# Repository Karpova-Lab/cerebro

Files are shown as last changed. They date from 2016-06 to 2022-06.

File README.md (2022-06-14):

# Cerebro Wireless Optogenetics System v2

Detailed documentation at [https://karpova-lab.github.io/cerebro/](https://karpova-lab.github.io/cerebro/)

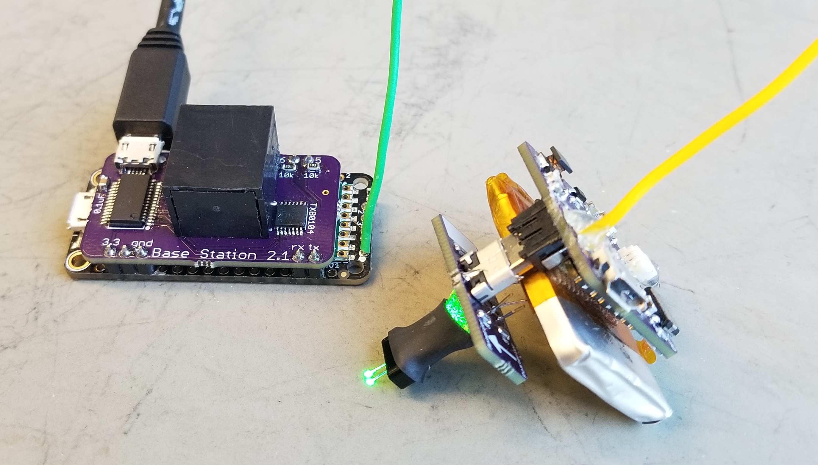
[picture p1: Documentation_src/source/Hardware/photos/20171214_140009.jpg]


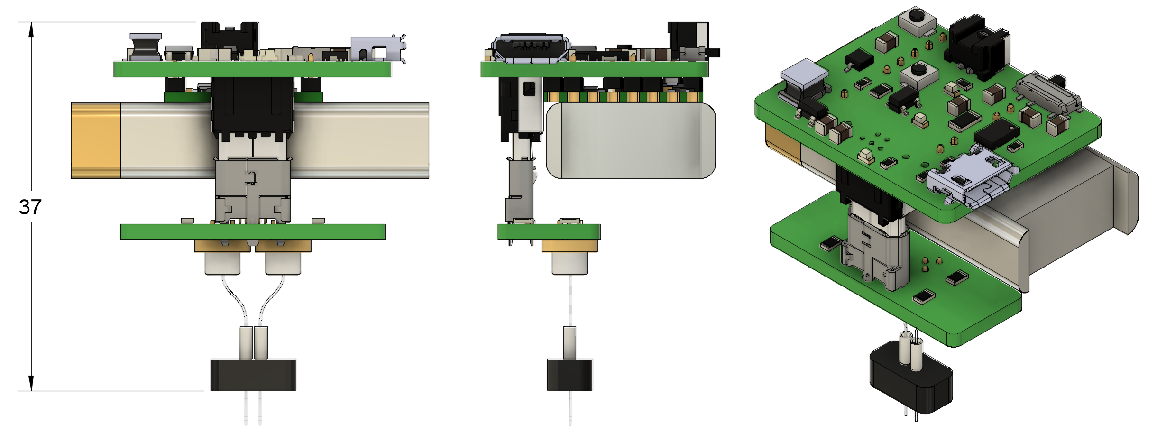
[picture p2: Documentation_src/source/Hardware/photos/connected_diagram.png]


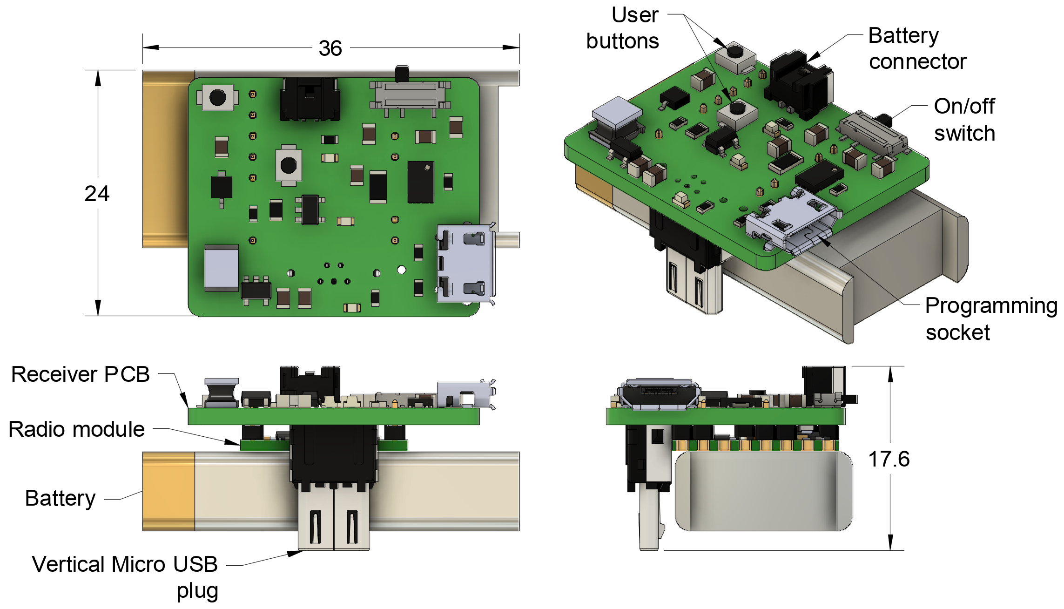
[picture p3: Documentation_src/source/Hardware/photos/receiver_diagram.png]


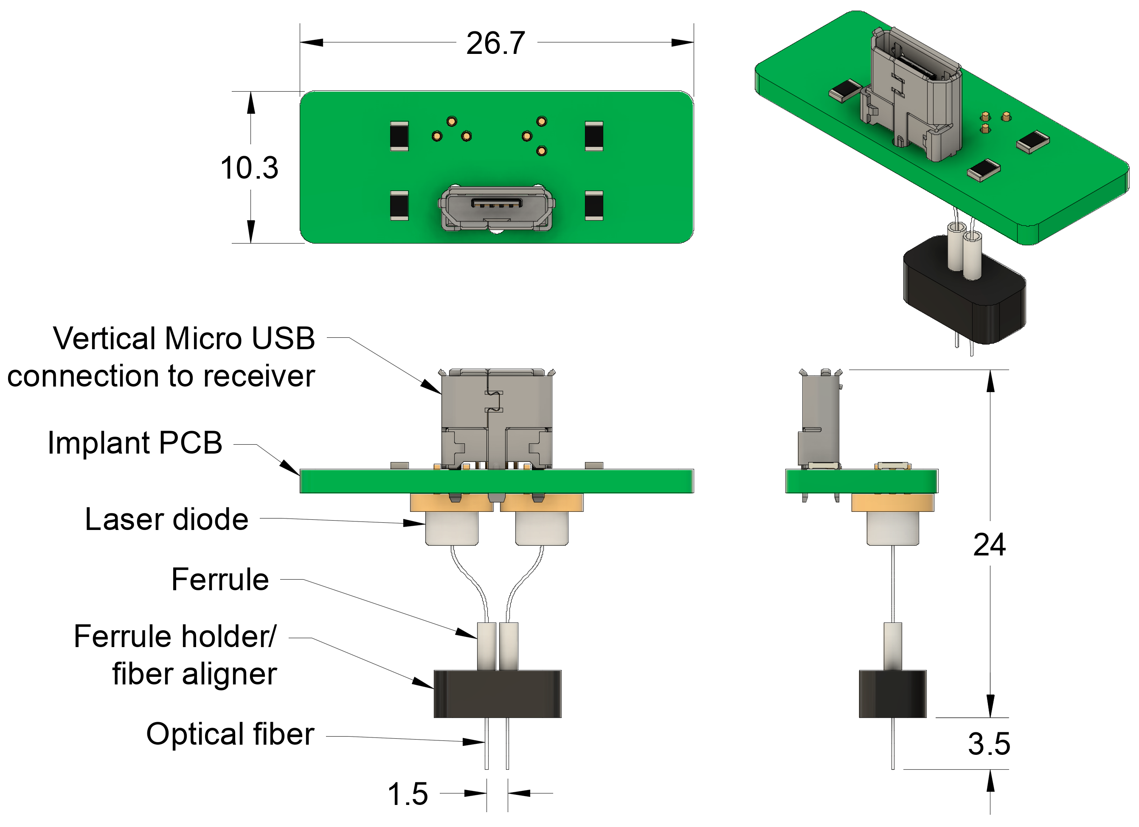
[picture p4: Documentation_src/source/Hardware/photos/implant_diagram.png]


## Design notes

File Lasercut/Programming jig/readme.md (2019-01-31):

# Bill of Materials
- [Spear head pogo pins](https://www.adafruit.com/product/394)
- [Toggle clamp](https://www.adafruit.com/product/2457)
- M6 x 20mm Pan head screws
- M6 nuts
- 1/8" Acrylic

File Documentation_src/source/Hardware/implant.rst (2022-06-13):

:github_url: https://github.com/Karpova-Lab/cerebro

============
Head Implant
============
.. include:: Characters/isogrk1.txt
.. include:: Characters/mmlalias.txt
.. include:: Characters/isopub.txt

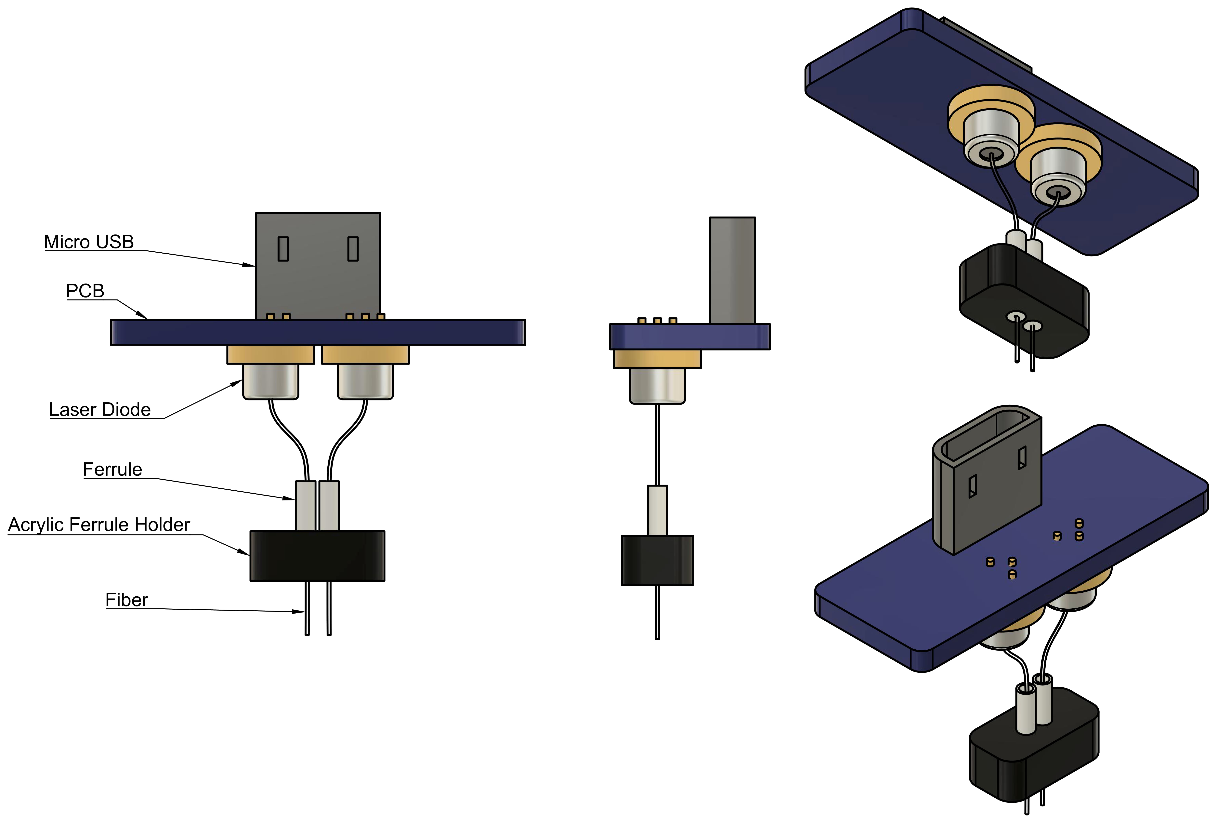
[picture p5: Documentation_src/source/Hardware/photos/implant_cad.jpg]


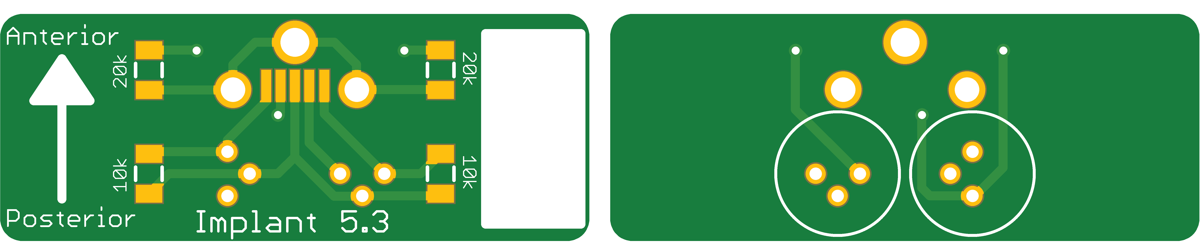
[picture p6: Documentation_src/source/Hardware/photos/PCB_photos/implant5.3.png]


  `Click Here for Design Files <https://github.com/Karpova-Lab/cerebro/tree/master/PCB%20Files/Implant%205.3>`_ 

.. _implantTools:

Required Tools
==============
  * Ruler
  * Soldering iron
  * Tweezers   
  * `Fiber gripper <https://www.thorlabschina.cn/thorproduct.cfm?partnumber=BFG1>`_ 
  * `Fiber stripper <https://www.thorlabs.com/thorProduct.cfm?partNumber=T12S21>`_
  * `Fiber cleaver <http://www.fiberinstrumentsales.com/fis-lynx-precision-cleaver-with-fiber-basket.html>`_
  * `3-axis fiber launch system <http://www.thorlabs.com/thorproduct.cfm?partnumber=MBT612D/M>`_
  * `Power meter <https://www.thorlabs.com/thorproduct.cfm?partnumber=PM121D>`_ and `photodiode sensor <https://www.thorlabs.com/thorproduct.cfm?partnumber=S121C>`_
  * `Adjustable DC Power Supply <https://www.amazon.com/KORAD-KD3005D-Precision-Adjustable-Regulated/dp/B00FPU6G4E/ref=sr_1_2?s=hi&ie=UTF8&qid=1521832325&sr=1-2&keywords=korad+power+supply&dpID=41CeDR0WTPL&preST=_SY300_QL70_&dpSrc=srch>`_ 
  * `Ultraviolet light <https://www.amazon.com/TaoTronics-TT-FL001-Flashlight-Blacklight-Ultraviolet/dp/B00RV8PREI/ref=sr_1_1?ie=UTF8&qid=1484071557&sr=8-1&keywords=B00RV8PREI>`_

Bill of Materials
=================
+-----+-----------------------------+----------------------------------------------------------------+-------------------------------------------------------------------------------------------------------------------------+
| Qty | Description                 | Datasheet                                                      | Order Link                                                                                                              | 
+=====+=============================+================================================================+=========================================================================================================================+
| 1   | Implant PCB                 |  :download:`Implant 5.3<Datasheets/implant_5.3.pdf>`           | `OSH Park <https://oshpark.com/shared_projects/k8Ikpli6>`__                                                             | 
+-----+-----------------------------+----------------------------------------------------------------+-------------------------------------------------------------------------------------------------------------------------+
| 1   | Laser Diode                 |  :download:`PLT5 520_B1_2_3<Datasheets/green_laser_diode.pdf>` | `World Star Tech <http://www.worldstartech.com/products/laser-diodes/green-laser-diode-osram/>`__                       | 
+-----+-----------------------------+----------------------------------------------------------------+-------------------------------------------------------------------------------------------------------------------------+
| 1   | Fiber                       | F-MBB                                                          | `Newport <https://www.newport.com/p/F-MBB>`__                                                                           | 
+-----+-----------------------------+----------------------------------------------------------------+-------------------------------------------------------------------------------------------------------------------------+
| 1   | UV curing adhesive          |  :download:`NOA 68<Datasheets/uv_adhesive.pdf>`                | `Norland Products <https://www.norlandproducts2.com/adhesives/adproductsdetail_header_removed.asp?Prdid=68>`__          | 
+-----+-----------------------------+----------------------------------------------------------------+-------------------------------------------------------------------------------------------------------------------------+
| 1   | Ferrule                     |  :download:`MM-FER2007C<Datasheets/ferrule.pdf>`               | `Precision Fiber Products <https://precisionfiberproducts.com/pfp-lc-1-25mm-od-multimode-ceramic-zirconia-ferrules/>`__ | 
+-----+-----------------------------+----------------------------------------------------------------+-------------------------------------------------------------------------------------------------------------------------+
| 1   | Epoxy                       |  :download:`T120023C<Datasheets/epoxy.pdf>`                    | `Fiber Instrument Sales <http://www.fiberinstrumentsales.com/fis-room-cure-epoxy-2-grams.html>`__                       | 
+-----+-----------------------------+----------------------------------------------------------------+-------------------------------------------------------------------------------------------------------------------------+
| 2   | Micro USB vertical socket   |  :download:`1051330011<Datasheets/usb_socket_vertical.pdf>`    | `Digi-Key <https://www.digikey.com/products/en?keywords=WM10134CT-ND>`__                                                | 
+-----+-----------------------------+----------------------------------------------------------------+-------------------------------------------------------------------------------------------------------------------------+
| 2   | Heat shrink tubing          |  :download:`HSTTV12-Y<Datasheets/heatshrink.pdf>`              | `Digi-Key <https://www.digikey.com/products/en?x=0&y=0&lang=en&site=us&keywords=298-11559-ND>`__                        | 
+-----+-----------------------------+----------------------------------------------------------------+-------------------------------------------------------------------------------------------------------------------------+
| 2   | 0603 10 k\ |OHgr| Resistor  |                                                                |                                                                                                                         | 
+-----+-----------------------------+----------------------------------------------------------------+-------------------------------------------------------------------------------------------------------------------------+
| 1   | 0603 20 k\ |OHgr| Resistor  |                                                                |                                                                                                                         | 
+-----+-----------------------------+----------------------------------------------------------------+-------------------------------------------------------------------------------------------------------------------------+

Assembly Instructions
=====================
Prepare Fiber
-------------
#. Tape down the fiber
#. Use a fiber stripper to remove the outer blue jacket from the fiber

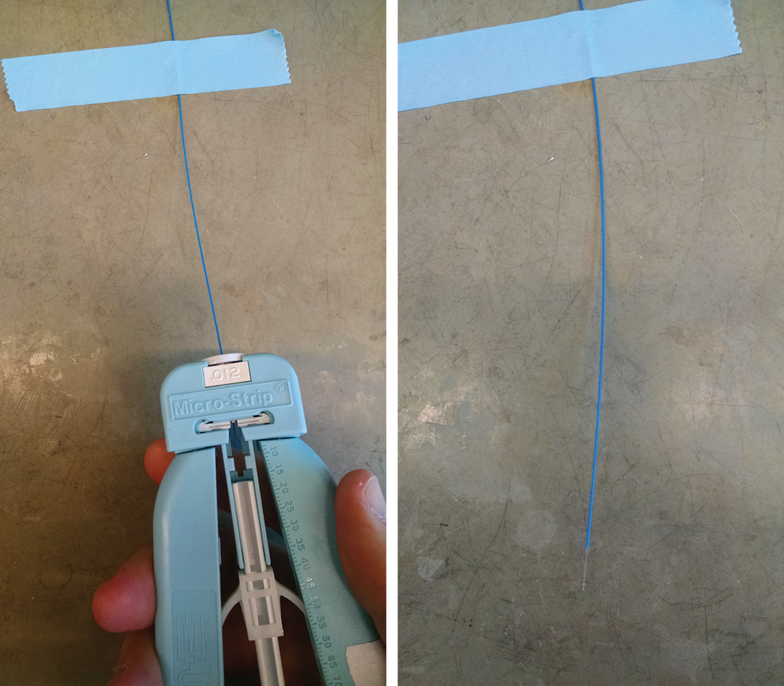
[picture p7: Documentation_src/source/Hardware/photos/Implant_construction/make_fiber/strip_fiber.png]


3. Using a fiber cleaver, cut off the end of fiber to make a clean tip
#. Continue cutting the fiber into ~16mm pieces

Align Fiber
-----------
#. Insert laser diode into connector
#. Place connector in alignment jig
#. Place fiber in alignment jig
#. Turn on the power meter and connect to computer over usb
#. Open up the `Thorlabs' Power Meter Software <https://www.thorlabs.com/software_pages/ViewSoftwarePage.cfm?Code=PM100x>`_ 
#. Establish the USB connection with Power meter by selecting the device and clicking "OK"

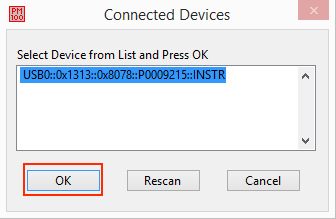
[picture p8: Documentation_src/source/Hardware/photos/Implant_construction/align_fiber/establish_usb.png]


7. Adjust the following settings:

  - Range: 12mW
  - Wave: 520nm
  - Log Configuration

    - No of Samples: 20,000
    - Interval Time: 0.1

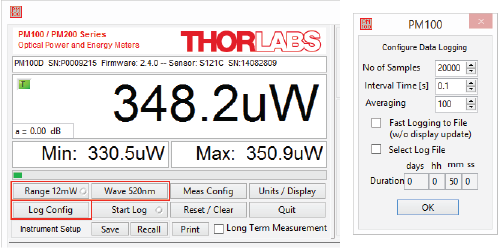
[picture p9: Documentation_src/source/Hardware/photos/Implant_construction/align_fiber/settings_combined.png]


8. Click ``Start Log``



9. Set the power supply to 8.0 volts with a current limit of 300 mA
#. Provide power to the laser diode by pressing the "on/off" button
#. While watching the power graph update, use the `3-axis fiber launch system <http://www.thorlabs.com/thorproduct.cfm?partnumber=MBT612D/M>`_ to adjust the x, y, and z alignment of the fiber with respect to the laser diode.
#. When you are happy with the alignment, apply UV curing adhesive to the fiber/laserdiode junction.
#. Cure the adhesive using UV light

Fiber Guide Construction
------------------------
A fiber guide is needed to ensure that the fibers are at a precise distance apart, and are parallel. The distance will depend on what area of the brain is being targeted. Below are files for 1.5 mm and 2.74 mm gap between fibers.

- :download:`Fiber guide_1,5mm gap.dxf<../../../Lasercut/Fiber guide/Fiber guide_1,5mm gap.dxf>` 
- :download:`Fiber guide_1,5mm gap.ai<../../../Lasercut/Fiber guide/Fiber guide_1,5mm gap.ai>` 
- :download:`Fiber guide_2,74mm gap.ai<../../../Lasercut/Fiber guide/Fiber guide_2,74mm gap.ai>` 

The laser cutter speed and power settings may need to be tweaked to get a good fit for the the ceramic ferrules.

#. Insert the ceramic ferrules into the acrylic fiber guide. The flat side of the ferrules should be flush with the face of the acrylic.

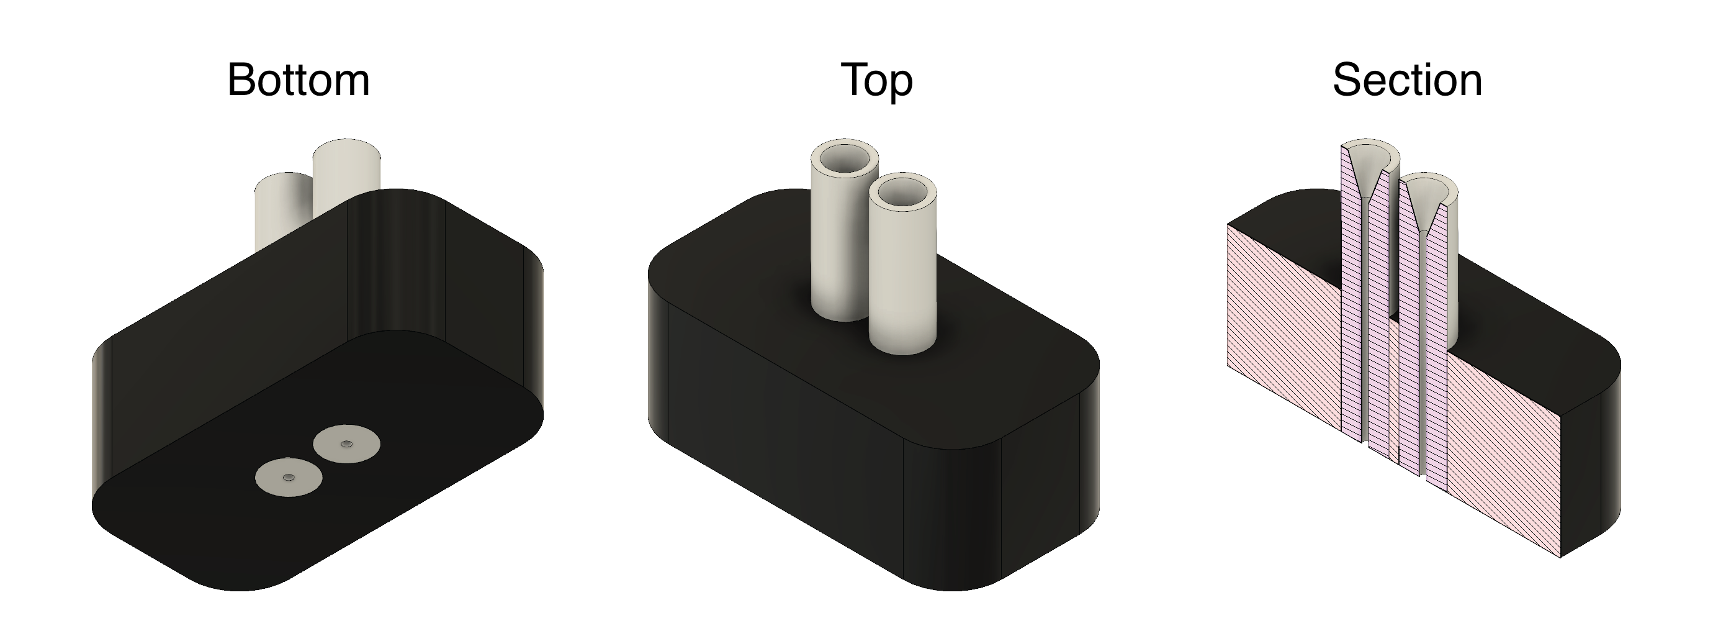
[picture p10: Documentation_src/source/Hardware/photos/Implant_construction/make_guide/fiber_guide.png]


Combine PCB, Laser Diodes, and Fiber Guide
------------------------------------------
#. Solder the vertical microusb connector onto the PCB
#. Solder 1 leg of each laser diode onto the PCB
#. Bend the laser diodes toward eachother so the tips of the fiber slightly intersect near their tips
#. Solder the remaining legs of the laser diodes
#. Cut ~10mm of heat shrink tubing and slide it onto one of the laser diodes
#. Apply heat to the heat shrink tubing

.. Warning::
   Heat can weaken the UV glue that is used to attach the fiber. Be careful not to apply too much heat for too long as you may risk weakening the glue, causing the fiber to move out of alignment or detach completely.

7. Slide the fiber guide onto the two fibers. Adjust the 
#. Surround the fibers and laser diodes with epoxy
#. Place heatshrink tubing around the clear epoxy section of the implant
#. Place and solder the remaining resistors onto the PCB

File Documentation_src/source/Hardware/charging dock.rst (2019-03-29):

:github_url: https://github.com/Karpova-Lab/cerebro

=============
Charging Dock 
=============

.. include:: Characters/isogrk1.txt
.. include:: Characters/mmlalias.txt

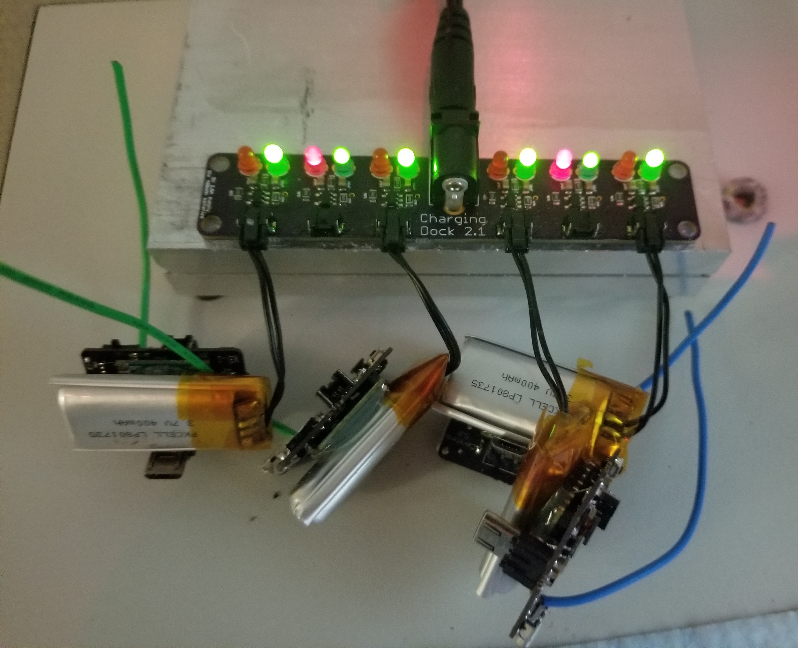
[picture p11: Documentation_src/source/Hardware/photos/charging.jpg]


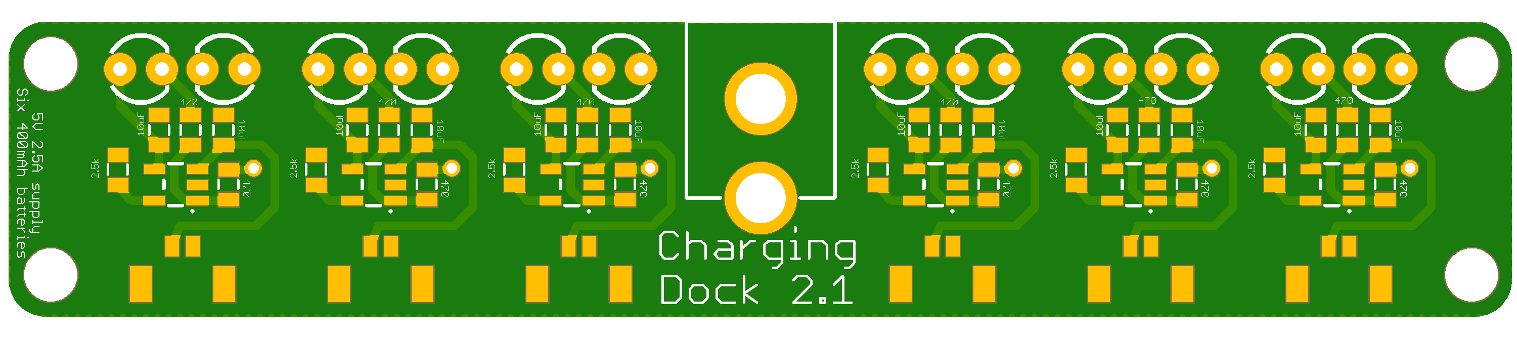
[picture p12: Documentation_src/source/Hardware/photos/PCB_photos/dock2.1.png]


  `Click Here for Design Files <https://github.com/Karpova-Lab/cerebro/tree/master/PCB%20Files/Charging%20Dock%202.1>`_ 

Bill of Materials
=================

+-----+------------------------------+------------------------------------------------------------------+----------------------------------------------------------------------------------------------------+
| Qty | Description                  | Datasheet                                                        | Order Link                                                                                         | 
+=====+==============================+==================================================================+====================================================================================================+
| 1   | Charging Dock PCB            |  :download:`Charging Dock 2.0<Datasheets/charging_dock_2.0.pdf>` | `OSH Park <https://oshpark.com/shared_projects/hz6upCEq>`__                                        | 
+-----+------------------------------+------------------------------------------------------------------+----------------------------------------------------------------------------------------------------+
| 1   | Molex Micro-Lock socket      |  :download:`5055670271<Datasheets/microlock_socket.pdf>`         | `Digi-Key <https://www.digikey.com/products/en?keywords=WM17038CT-ND>`__                           | 
+-----+------------------------------+------------------------------------------------------------------+----------------------------------------------------------------------------------------------------+
| 6   | Lipoly Charging IC           |  :download:`MCP73831T-2ACI/OT<Datasheets/lipo_charger.pdf>`      | `Digi-Key <https://www.digikey.com/products/en?keywords=%09MCP73831T-2ACI%2FOTCT-ND>`__            | 
+-----+------------------------------+------------------------------------------------------------------+----------------------------------------------------------------------------------------------------+
| 1   | DC Barrel Power Jack         |  :download:`PJ-037A<Datasheets/power_jack.pdf>`                  | `Digi-Key <https://www.digikey.com/products/en?keywords=cp-037a-nd>`__                             | 
+-----+------------------------------+------------------------------------------------------------------+----------------------------------------------------------------------------------------------------+
| 1   | 5V 2.5A Power Supply         |  :download:`SWI12-5-N-P5R<Datasheets/power_supply.pdf>`          | `Digi-Key <https://www.digikey.com/product-detail/en/cui-inc/SWI12-5-N-P5R/102-3425-ND/5287234>`__ | 
+-----+------------------------------+------------------------------------------------------------------+----------------------------------------------------------------------------------------------------+
| 6   | Green LED                    |  :download:`151031VS06000<Datasheets/led_3mm_green.pdf>`         | `Digi-Key <https://www.digikey.com/products/en?keywords=732-5008-ND>`__                            | 
+-----+------------------------------+------------------------------------------------------------------+----------------------------------------------------------------------------------------------------+
| 6   | Red LED                      |  :download:`151031SS06000<Datasheets/led_3mm_red.pdf>`           | `Digi-Key <https://www.digikey.com/products/en?keywords=732-5006-ND>`__                            | 
+-----+------------------------------+------------------------------------------------------------------+----------------------------------------------------------------------------------------------------+
| 12  | 0805 470 \ |OHgr| Resistor   |                                                                  |                                                                                                    | 
+-----+------------------------------+------------------------------------------------------------------+----------------------------------------------------------------------------------------------------+
| 6   | 0805 2.5 K\ |OHgr| Resistor  |                                                                  |                                                                                                    | 
+-----+------------------------------+------------------------------------------------------------------+----------------------------------------------------------------------------------------------------+
| 12  | 0805 10 |mgr|\F Capacitor    |                                                                  |                                                                                                    | 
+-----+------------------------------+------------------------------------------------------------------+----------------------------------------------------------------------------------------------------+

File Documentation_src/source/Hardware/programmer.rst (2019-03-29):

:github_url: https://github.com/Karpova-Lab/cerebro

==============
Pogo Connector
==============

.. include:: Characters/isogrk1.txt
.. include:: Characters/mmlalias.txt

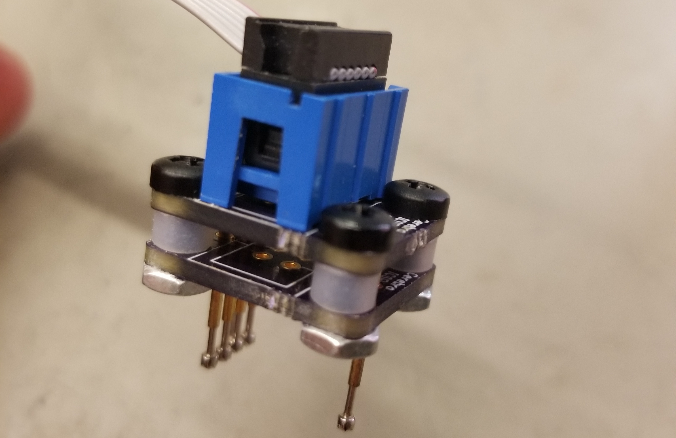
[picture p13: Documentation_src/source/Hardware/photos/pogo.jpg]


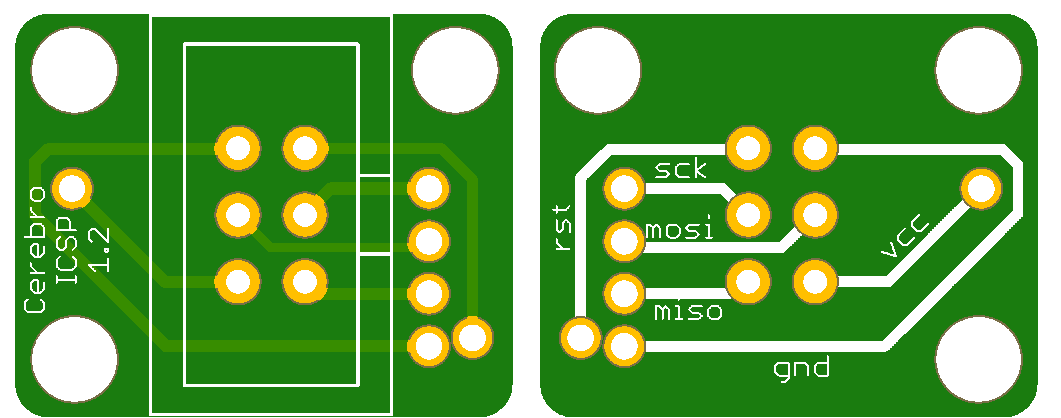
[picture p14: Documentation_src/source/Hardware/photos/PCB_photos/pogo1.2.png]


  `Click Here for Design Files <https://github.com/Karpova-Lab/cerebro/tree/master/PCB%20Files/Cerebro%20ICSP%201.2>`_ 

Bill of Materials
=================

+-----+----------------------+-------------------------------------------------------+-------------------------------------------------------------------------+
| Qty | Description          | Datasheet                                             | Order Link                                                              | 
+=====+======================+=======================================================+=========================================================================+
| 2   | Programmer PCB       | Cerebro ICSP 1.2                                      | `OSH Park <https://oshpark.com/shared_projects/PXMM4F8R>`__             | 
+-----+----------------------+-------------------------------------------------------+-------------------------------------------------------------------------+
| 1   | 6 Pin Socket         |  :download:`75869-331LF<Datasheets/ICSP_socket.pdf>`  | `Digi-Key <https://www.digikey.com/products/en?keywords=609-5122-ND>`__ | 
+-----+----------------------+-------------------------------------------------------+-------------------------------------------------------------------------+
| 5   | Spear Head Pogo Pin  | 394                                                   | `Adafruit <https://www.adafruit.com/product/394>`__                     | 
+-----+----------------------+-------------------------------------------------------+-------------------------------------------------------------------------+
| 1   | Needle Head Pogo Pin | 2430                                                  | `Adafruit <https://www.adafruit.com/product/2430>`__                    | 
+-----+----------------------+-------------------------------------------------------+-------------------------------------------------------------------------+
| 3   | M3 x 0.5 Screw       |  :download:`92492A717<Datasheets/m3_nylon_screw.pdf>` | `McMaster-Carr <https://www.mcmaster.com/#92492A717>`__                 | 
+-----+----------------------+-------------------------------------------------------+-------------------------------------------------------------------------+
| 3   | Nylon Spacer         |  :download:`93657A203<Datasheets/nylon_spacer.pdf>`   | `McMaster-Carr <https://www.mcmaster.com/#93657A203>`__                 | 
+-----+----------------------+-------------------------------------------------------+-------------------------------------------------------------------------+
| 3   | M3 Nut               |  :download:`90695A033<Datasheets/m3_nut.pdf>`         | `McMaster-Carr <https://www.mcmaster.com/#90695A033>`__                 | 
+-----+----------------------+-------------------------------------------------------+-------------------------------------------------------------------------+

Use the Pogo connector to :ref:`burn a bootloader onto Cerebro <burn boot>`

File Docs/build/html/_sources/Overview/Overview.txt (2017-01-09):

================
System Overview
================
.. include:: isogrk1.txt
.. include:: mmlalias.txt

Features
--------

Open Source = Flexible
  All code and CAD is available so you can make changes and improvements to anything you want!

Low Latency
  Less than 3ms latency between a trigger command being sent and the laser diodes being powered on.

Wirelessly Adjustable Waveforms
  Cerebro can be produce :ref:`customizable waveforms<waveform parameters>` with 1ms resolution. The waveform parameters can be adjusted wirelessly, even while the animal is behaving.

Laser Diodes
  Laser diodes are more powerful than LEDs. Instead of using a LED coupled to a large fiber, you can use a laser diode coupled to smaller fiber and get equivalent light power output but with reduced brain tissue damage.
  Bilateral implants have been capable of up to 15 mW per fiber-coupled laser diode or 450 mW/mm\ :sup:`2` (tested with two 520 nm laser diodes coupled to 200 |mgr|\m diameter fibers and powered by two 105 mAh lipo batteries).

.. Keep in mind the limiting factor of the tested implant wasn't the laser diodes, but rather the peak current supply of the batteries.

.. This means you can substitute a LED coupled to a large fiber, with a laser diode coupled to smaller (less brain damaging) fiber.
.. By coupling high power laser diodes with small fibers, one can get the same amount of light power
.. as LEDs coupled with large fibers, but instead use a high power laser diode with a small fiber. Using smaller fibers results in less brain tissue damage.
..
.. One can get equal light power by coupling high power laser diodes with small fibers, as one

Low Material Cost
  Hardware BOMs are provided, with a total estimated cost of $300. The software is free.

.. csv-table::
  :header: "Subsystem", "Material Cost ($)", "Assembly Time (hours)"
  :widths: 1,1,1

  Cerebro,30 , 1
  Head Implant (bilateral),190,4
  Base Station,5,1
  IR Remote,40,1
  Arduino + Utility Shield,30,1
  Downloader Cord,5,1
  Xavier, FREE, 0
  ,
  **Total**,**$300**,**9 hours**

Commercial Alternatives
-----------------------
Here are some commercial products that also provide wireless optogenetics:

| `Eicom Teleopto <https://eicomusa.com/teleopto/>`_
| `Kendall Research Systems <http://www.kendallresearchsys.com/>`_
| `Neurolux <http://www.neurolux.org/products/>`_
| `Triangle Biosystems <http://www.trianglebiosystems.com/s-series-systems.html>`_
|

.. .. csv-table::
..   :header: "Product", "Cost ($)", "Features"
..   :widths: 1,1,1
..
..   `Eicom Teleopto <https://eicomusa.com/teleopto/>`_ , "4,500", "Very similar to Cerebro. Uses battery and IR triggering."
..   `Kendall Research Systems <http://www.kendallresearchsys.com/>`_ , "20,000", "Uses wireless power. Includes 3-axis accelerometer"
..   `Neurolux <http://www.neurolux.org/products/>`_,
..   `Triangle Biosystems <http://www.trianglebiosystems.com/s-series-systems.html>`_,

Cerebro
-------

.. image:: cerebro.jpg
  :align: center
  :scale: 20 %

Cerebro is a rechargable wireless receiver that connects to a head implant assembly. Cerebro receives commands from a :ref:`base station` and delivers power to
the laser diodes on the head implant, resulting in light being emitted through the optical fibers into the brain. The
intensity and waveform of the emitted light can be adjusted wirelessly during an experiment (:ref:`How to change Pulse Parameters <pulse change header>`).
All commands sent to Cerebro are saved along with timestamps to onboard non-volatile memory.

:doc:`More info... <../Hardware/cerebro>`

Head Implant
------------

.. image:: implant.jpg
  :align: center
  :scale: 10 %

The head implant assembly consists of two laser diodes coupled to optical fibers. Also included is a photoresistor that is used as feedback
to maintain a constant light output.

:doc:`More info... <../Hardware/implant>`

.. _base station:

Base Station
------------
.. image:: base_station.jpg
  :align: center
  :scale: 15 %

The Base Station is responsible for emitting infrared light signals to communicate wirelessly with Cerebro (exactly like a TV remote).
It is connected by USB to a Windows computer, where commands can be sent and events can be logged using :ref:`Xavier <xavier>`.
Base Station can also be controlled directly by `TTL <https://learn.sparkfun.com/tutorials/logic-levels#ttl-logic-levels>`_ signals going into
its RJ45 connector. A high TTL signal on pin3 of the RJ45 causes a trigger signal to be emitted, and a high TTL signal on pin2 causes
a stop signal to be emitted. Events will still be logged by Xavier even when triggered by a TTL.

:doc:`More info... <../Hardware/implant>`

.. _utility shield:

Utility Shield
--------------
.. image:: utility_shield.jpg
  :align: center
  :scale: 15 %

The Utility Shield connects to an `Arduino Uno <https://www.arduino.cc/en/main/arduinoBoardUno>`_ and is used to flash programs to a variety of AVR microcontrollers.
It can flash the ATtiny84 DIP used by the IR Remote and Charging Dock, the ATtiny84 SOIC used by Cerebro, the ATtiny85 DIP used by the Base Station, and the ATmega328P
used by the IR Remote. The shield also provides a charging port for Cerebro that has a green/red charging indicator light.

:doc:`More info... <../Hardware/utility shield>`

Charging Dock
-------------
.. image:: charging_dock.jpg
  :align: center
  :scale: 20 %

The Charging Dock provides ports for charging up to 4 Cerebro receivers at one time.
An OLED display shows the voltages of the batteries being charged.
A red indicator LED is lit while Cerebro is charging, and turns off once Cerebro is fully charged.

:doc:`More info... <../Hardware/charging dock>`

IR Remote
---------

.. image:: IR_remote.jpg
  :align: center
  :scale: 20 %

The IR Remote is a handheld remote that can be used to send commands to Cerebro.
Information including battery status, current parameters, and ID number can be checked by plugging a Cerebro Receiver into the IR Remote.

:doc:`More info... <../Hardware/remote>`

.. _cord:

Downloader Cord
---------------
.. image:: downloader.jpg
  :align: center
  :scale: 15 %

The Downloader Cord is used for serial communication between a computer and Cerebro. Once connected to Cerebro's
micro usb port, it can be used for downloading log data off of Cerebro's EEPROM, or it can be used to display
messages when Cerebro is in debugging mode.

:doc:`More info... <../Hardware/downloader cord>`

.. _xavier:

Xavier
------

.. image:: xavier_demo.png
    :align: center
    :scale: 80 %

Xavier is a GUI for sending and logging Base Station commands. Since communication between Cerebro and Base Station is unidirectional, in order to truly know what occurs throughout an experiment,
every event that is received by Cerebro is also saved to an onboard log.  After an experiment is complete, Cerebro's onboard logfile can be
downloaded into Xavier. The two log files can then be saved and analyzed to confirm that everything that was sent by Base Station was in fact received and executed by Cerebro.
Xavier provides an easy interface for sending parameter changes and can also be used a debugging tool.

:doc:`More info... <../Software/Xavier>`

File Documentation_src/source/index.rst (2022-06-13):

:github_url: https://github.com/Karpova-Lab/cerebro

.. include:: isogrk1.txt
.. include:: mmlalias.txt

========================================
Cerebro Wireless Optogenetics System v2
========================================

Welcome! This is the hardware and software documentation of a system used for wireless `optogenetic <https://en.wikipedia.org/wiki/Optogenetics>`_ stimulation.
As an `open-source <http://www.oshwa.org/definition/>`_ project, this documentation is intended to provide exhaustive resources and detailed instructions to enable anyone to
study, replicate, share, improve and contribute back to the Cerebro Wireless Optogenetics System. 

This project was developed by Andy Lustig in the `Karpova Lab <https://www.janelia.org/lab/karpova-lab>`_ at HHMI's Janelia Research Campus. If you have questions or comments, you can post them on the `discussions page <https://github.com/Karpova-Lab/cerebro/discussions>`_.

.. Note::
  You are currently viewing documentation for the **radio controlled Version 2 system**. 
  To view documentation for the **infrared controlled Version 1 system**, click the button below.

  .. raw:: html

    <div style="text-align:center; margin-bottom:24px">
      <a href="https://cerebro.readthedocs.io/en/1.0/" style="
      background-color: #6ab0de;
      border: none;
      color: white;
      padding: 10px 10px;
      text-align:center;
      text-decoration: none;
      display: inline-block;
      font-size: 20px;
      font-weight: bold;
      line-height: 1.1;
      border-radius:15px">
      Version 1 (infrared) documentation</a>
    </div>

.. _overview:

Features
========

Wireless Radio
  - **Low Latency** -  Less than 1.5 ms latency between a trigger command being sent and the laser diodes being powered on.
  - **2-Way Communication** - Base Station can send messages to start, extend, or interrupt light stimulation on Cerebro. Cerebro can send acknowledgment messages that commands are received, as well as battery status updates.
  - **Good Signal Range** - At least 20m, doesn't need line of sight. (The radio module that Cerebro uses has been shown to have ranges greater than 500m with the right antennas https://lowpowerlab.com/forum/rf-range-antennas-rfm69-library/rfm69hw-range-test!/)
  - **Wirelessly Adjustable Waveforms** - Cerebro can produce :ref:`customizable waveforms<waveform parameters>` with 1ms resolution. The waveform parameters can be adjusted wirelessly, even while the animal is behaving.

Laser Diodes
  - **High Power** - Laser diodes are more powerful than LEDs. Instead of using an LED coupled to a large fiber, you can use a laser diode coupled to smaller fiber and get equivalent light power output but with reduced brain tissue damage.
  - **Independent Bilateral Control of Intensity** -  Each laser diode has its own control circuitry, enabling you to turn on either diode at different times and/or different intensities. Intensity ramp-downs can be used to prevent post illumination rebounds in neural activity (https://www.cell.com/neuron/pdf/S0896-6273(17)30602-5.pdf).

Open Source
  * **Flexible** - All code and CAD is available so you can make changes and improvements to anything you want!
  * **Low Cost** - Hardware BOMs are provided, with a total estimated material cost of ~$200 (~$40 per Cerebro, ~$120 per bilateral head implant, ~$40 per Base Station). The software is free.
..    .. csv-table::
..      :header: "Subsystem", "Material Cost ($)", "Assembly Time (hours)"
..      :widths: 1,1,1
..    
..      Cerebro,40 , 2
..      Head Implant (bilateral),120,4
..      Base Station,40,.5
..      Xavier, FREE, 0
..      **Total**,**$145**,**6.5 hours**
  
.. **Technical Specifications**
.. 
.. .. csv-table::
..   :header: "Parameter", "Test Condition", "Value", "Unit"
..   :widths: 3,3,3,3
.. 
..   Weight,,13.2, g
..   Dimensions, Receiver, 0.68 x 0.74 x 0.062 , in
..             , Implant, 1.05 x 0.40 x 0.75, in
..   :download:`Battery Life <photos/battery new.html>`, "520nm, 8mW 3s pulse, 6 pulses/min ", 4.25 (1700), "hours (pulses)"
..   Recharge time, ,1 ,hour
..   Light Wavelength, ":download:`PLT5 520<Datasheets/PL520_B1.pdf>` (Green)", "520","nm"
..   :download:`Trigger Latency <photos/Signal_Breakdown.png>`, , 3.5 |pm|\  0.1, ms
..   Rise Time, , 10 , ms
..   Fiber Diameter, , 200,|mgr|\m
..   Light Output (per fiber) ,520 nm diode coupled to 200 |mgr|\m fiber, 0 to 15 |pm|\  0.5, mW
..   Input Voltage, , 3.5 to 4.2, V
..   Idle Current, ,"28","mA"

Block Diagram
=============

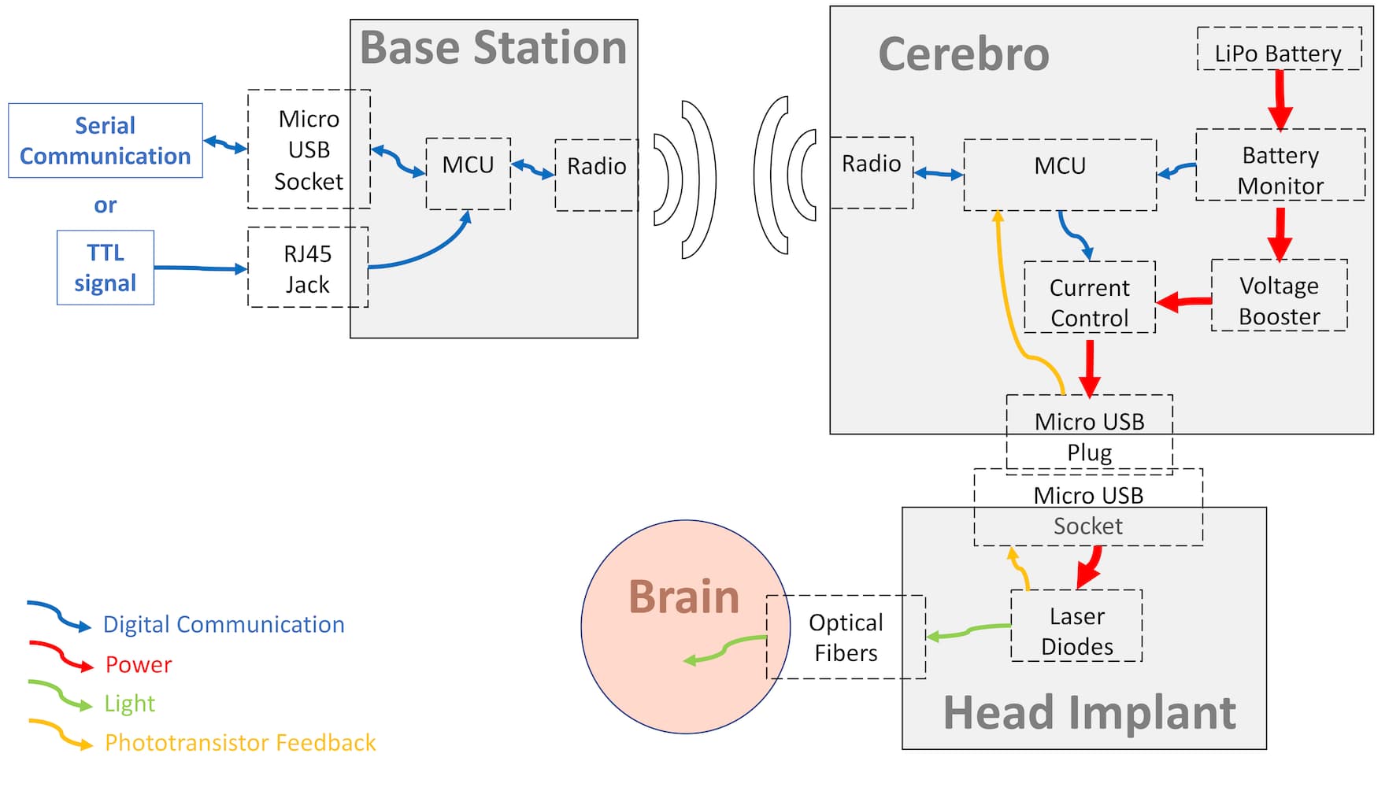
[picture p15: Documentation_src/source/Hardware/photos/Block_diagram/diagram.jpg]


System Components
=================
Cerebro
-------
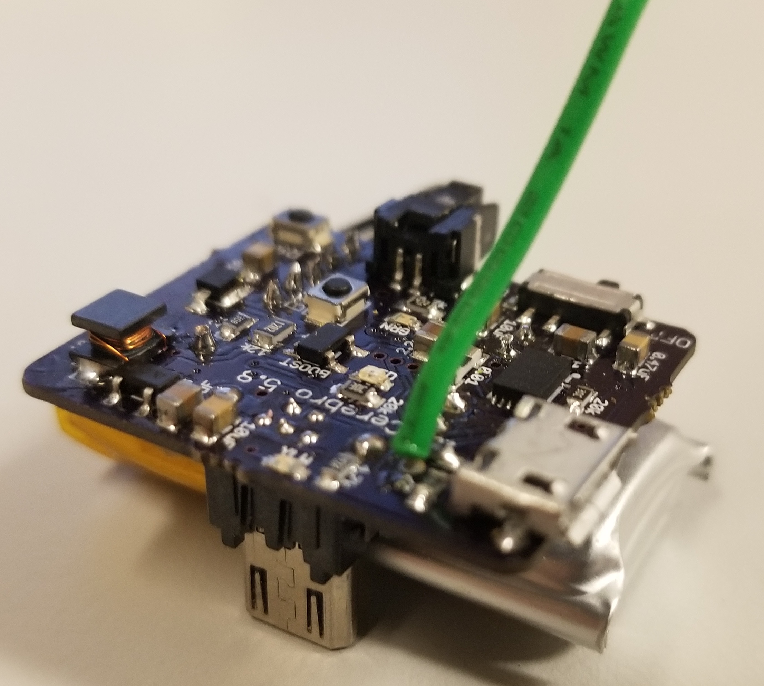
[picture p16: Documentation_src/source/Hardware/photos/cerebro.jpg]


Cerebro is a rechargable battery powered wireless receiver that connects to a head implant assembly. Cerebro receives commands from a :ref:`base station` and delivers power to
the laser diodes on the head implant, resulting in light being emitted through the optical fibers into the brain. The
intensity and waveform of the emitted light can be adjusted wirelessly during an experiment (:ref:`Edit Waveform Parameters <waveform parameters>`).

:doc:`More info... <Hardware/cerebro>`

Head Implant
------------


The head implant assembly consists of two laser diodes coupled to optical fibers. Both laser diodes include an integrated phototranistor that is used as feedback
to maintain a constant light output. The laser diodes can be independently controlled and can output arbitrary waveforms with millisecond resolution.

:doc:`More info... <Hardware/implant>`

.. _base station:

Base Station
------------
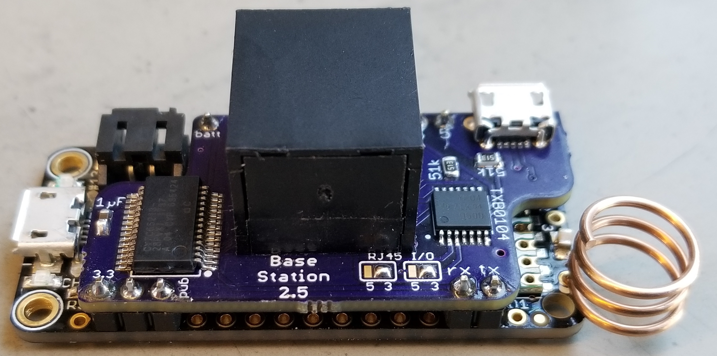
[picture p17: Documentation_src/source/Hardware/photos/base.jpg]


The Base Station is responsible for communicating wirelessly with Cerebro via radio.
It is connected by USB to a Windows computer, where commands can be sent and events can be logged using serial communication with Xavier.
Base Station can also be controlled directly by `TTL <https://learn.sparkfun.com/tutorials/logic-levels#ttl-logic-levels>`_ signals going into
its RJ45 connector. A high TTL signal on pin3 of the RJ45 causes a trigger command to be sent, and a high TTL signal on pin2 causes
a stop command to be sent.

:doc:`More info... <Hardware/base station>`

Charging Dock
-------------


The Charging Dock has the same battery connectors as Cerebro and can charge up to 6 Cerebro lipo batteries at once. 

:doc:`More info... <Hardware/charging dock>`

Xavier Software
---------------
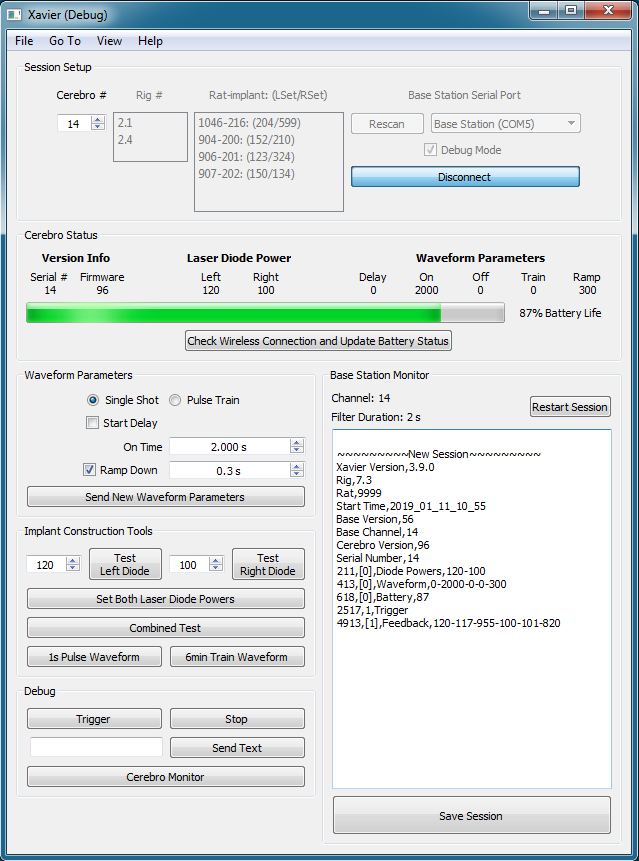
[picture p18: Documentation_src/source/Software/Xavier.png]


Xavier is a GUI for sending and logging Base Station commands. 
Xavier provides an easy interface for sending parameter changes and can also be used as a debugging tool.

:doc:`More info... <../Software/Xavier>`

Alternative Commerical Systems
==============================

Here are some commercial products that also provide wireless optogenetics:

- `Doric OSE System <https://neuro.doriclenses.com/collections/wireless-recording>`_ 
- `Eicom Teleopto <https://eicomusa.com/teleopto/>`_
- `Neurolux <http://www.neurolux.org/>`_
- `Multichannel Systems <https://www.multichannelsystems.com/products/wireless-systems>`_

Documentation Outline
=====================
.. toctree::
  :caption: Hardware

  Hardware/cerebro.rst
  Hardware/implant.rst
  Hardware/base station.rst
  Hardware/charging dock.rst
  Hardware/programmer.rst

.. toctree::
  :caption: Software

  Software/Xavier.rst

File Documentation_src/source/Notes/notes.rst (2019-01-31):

:github_url: https://github.com/Karpova-Lab/cerebro

====================
Additional Resources
====================

Soldering Tips
==============

Through Hole Soldering
----------------------

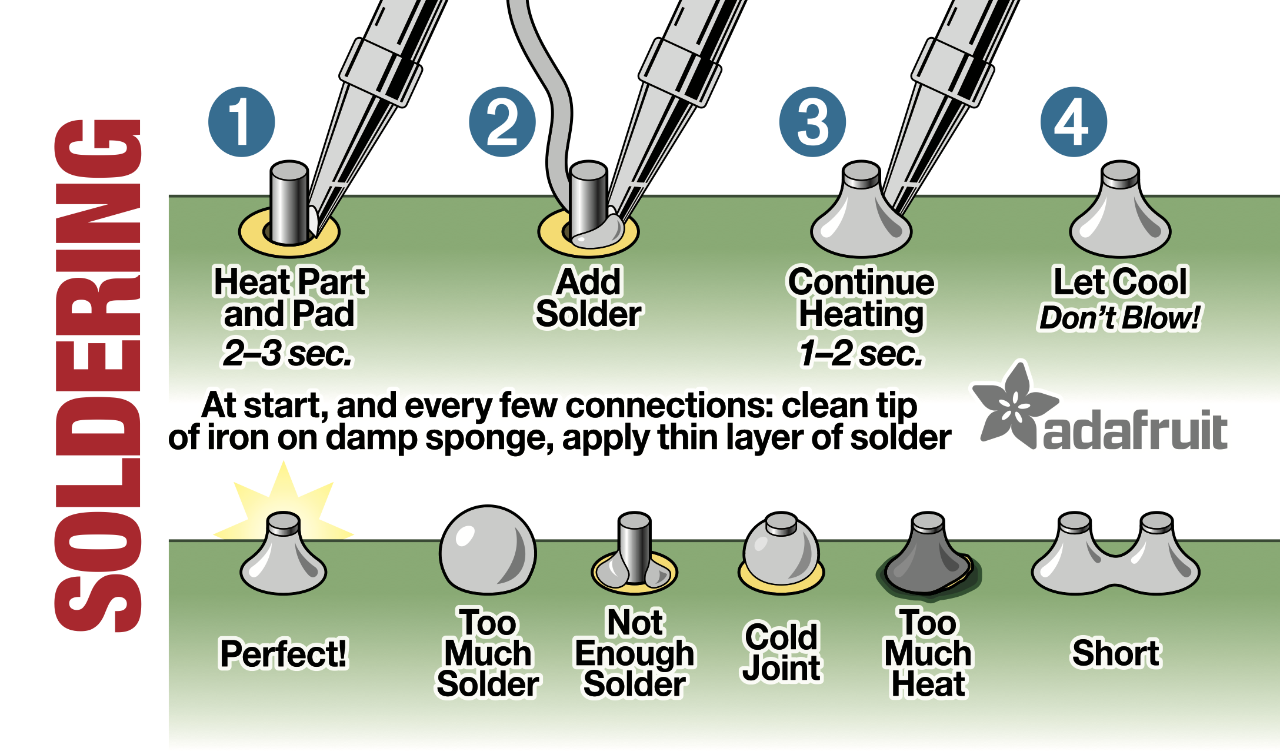
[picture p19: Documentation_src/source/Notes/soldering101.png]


Surface Mount Soldering
-----------------------

.. raw:: html

  <div style="text-align:center;margin-bottom:24px">
    <iframe width="560" height="315" src="https://www.youtube.com/embed/b9FC9fAlfQE?rel=0" frameborder="0" allowfullscreen></iframe>
  </div>

Git
===

Using Git
---------

Here is an nice introduction to what Git is: `Tutorial by Atlassian <https://www.atlassian.com/git/tutorials/what-is-version-control>`_

If you don't want to use the command line for running Git commands, I recommend downloading `SourceTree <https://www.sourcetreeapp.com/>`_ to use as a GUI.

Cloning the Cerebro repository from Github
------------------------------------------

From the Command Line
`````````````````````

Create a new folder into which you want to clone the repository

.. code::

   mkdir mylocalrepo

Navigate into the folder you just created and then clone the contents of the Cerebro repository from Github

.. code::

   cd mylocalrepo/
   git clone https://github.com/alustig3/Cerebro.git .

From a Mac terminal it will look like this:

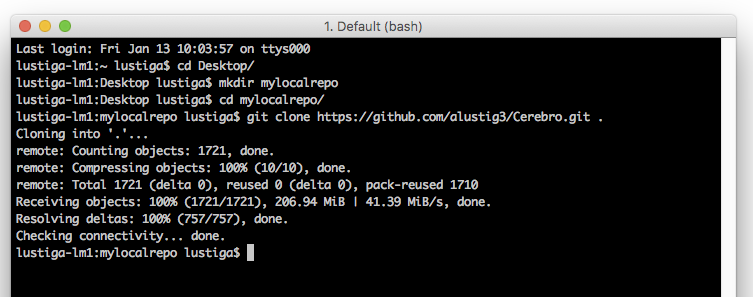
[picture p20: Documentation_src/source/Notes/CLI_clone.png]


Using SourceTree
````````````````
1. Navigate to File -> New/Clone
2. Paste ``https://github.com/alustig3/Cerebro.git`` as the source/URL
3. The files now exist locally on your computer

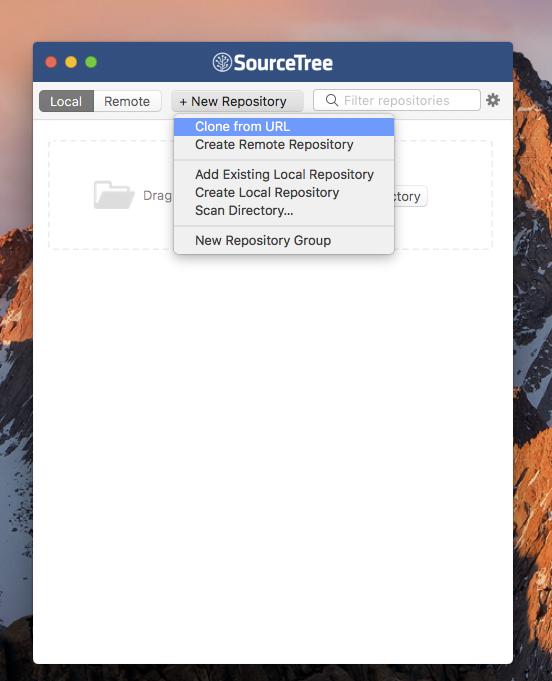
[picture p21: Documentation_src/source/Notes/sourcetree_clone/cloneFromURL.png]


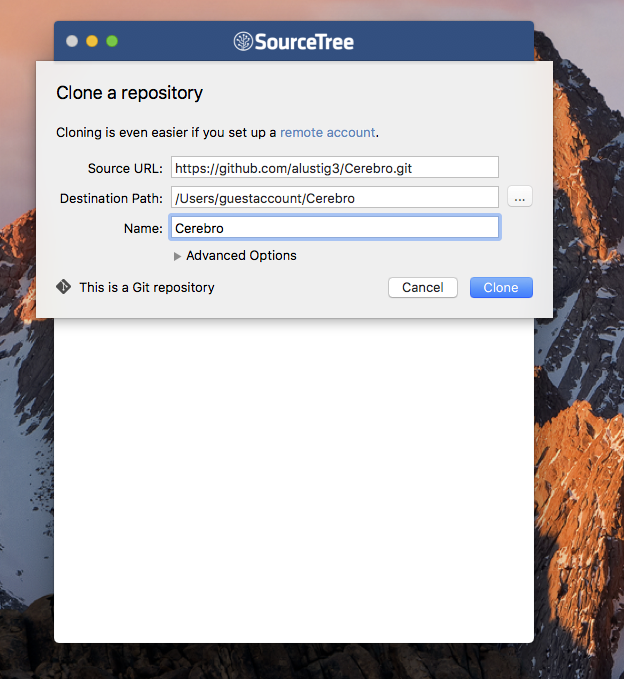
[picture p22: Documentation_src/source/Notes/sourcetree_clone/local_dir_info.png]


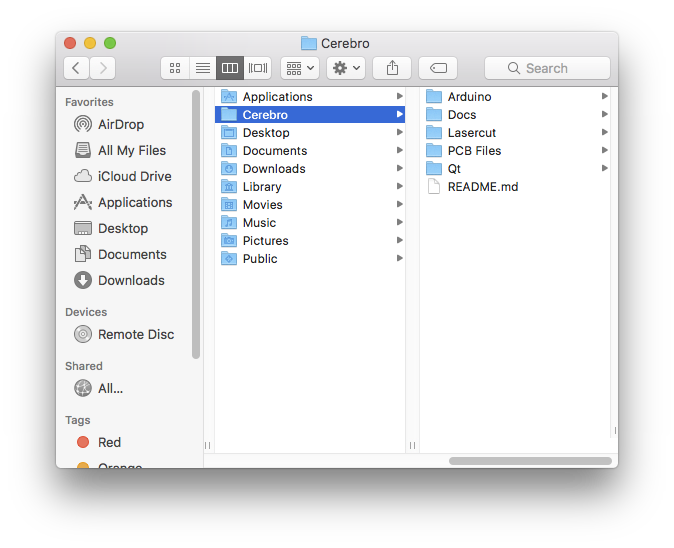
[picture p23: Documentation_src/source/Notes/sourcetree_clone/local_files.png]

  
Circuit Board Design
====================

EAGLE CAD design software is used for all of the circuit boards in the Cerebro Wireless Optogenetics System. To get started with editing PCB files, check out the following tutorials:

- `Jeremy Blum's EAGLE Tutorials <http://www.jeremyblum.com/category/eagle-tutorials/>`_
- `Sparkfun's Using EAGLE Series <https://learn.sparkfun.com/tutorials/using-eagle-schematic>`_

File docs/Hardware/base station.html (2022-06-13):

- Docs »
- Base Station
- Cerebro on GitHub (https://github.com/Karpova-Lab/cerebro)

Next Previous

# Base Station¶



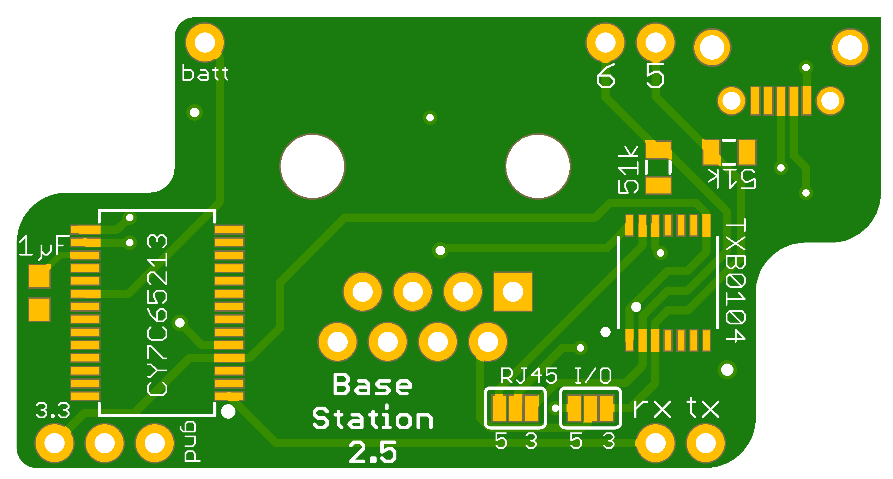
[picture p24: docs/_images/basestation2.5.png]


Click Here for Design Files (https://github.com/Karpova-Lab/cerebro/tree/master/PCB%20Files/Base%20Station%202.5)¶

## Bill of Materials¶

Qty | Description | Datasheet | Order Link
1 | Base Station PCB | Base Station 2.5 | OSH Park (https://oshpark.com/shared_projects/qpPpopqr)
1 | Feather 32u4 RFM69HCW | 3076 | Digi-Key (https://www.digikey.com/products/en?keywords=1528-1663-ND)
1 | USB to Serial Converter | CY7C65213-28PVXI | Digi-Key (https://www.digikey.com/products/en?keywords=%09CY7C65213-28PVXI-ND)
1 | Voltage Level Translator | TXB0104PWR | Digi-Key (https://www.digikey.com/products/en?keywords=296-21929-1-nd)
1 | Micro USB horizontal socket | 10118194-0001LF | Digi-Key (https://www.digikey.com/products/en?keywords=609-4618-1-ND)
1 | Antenna | HA.31.A | Digi-Key (https://www.digikey.com/products/en?keywords=931-1452)
2 | 0805 51 kΩ Resistor

## Downloads¶

- Cypress USB Driver (http://www.cypress.com/documentation/software-and-drivers/usb-serial-software-development-kit)
- Adafruit Feather Driver (https://learn.adafruit.com/adafruit-feather-32u4-basic-proto/using-with-arduino-ide)

Next Previous

© Copyright 2015-2022, Andy Lustig Last updated on Jun 13, 2022.

Built with Sphinx (http://sphinx-doc.org/) using a theme (https://github.com/rtfd/sphinx_rtd_theme) provided by Read the Docs (https://readthedocs.org).

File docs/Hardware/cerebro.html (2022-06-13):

- Docs »
- Cerebro
- Cerebro on GitHub (https://github.com/Karpova-Lab/cerebro)

Next Previous

# Cerebro¶

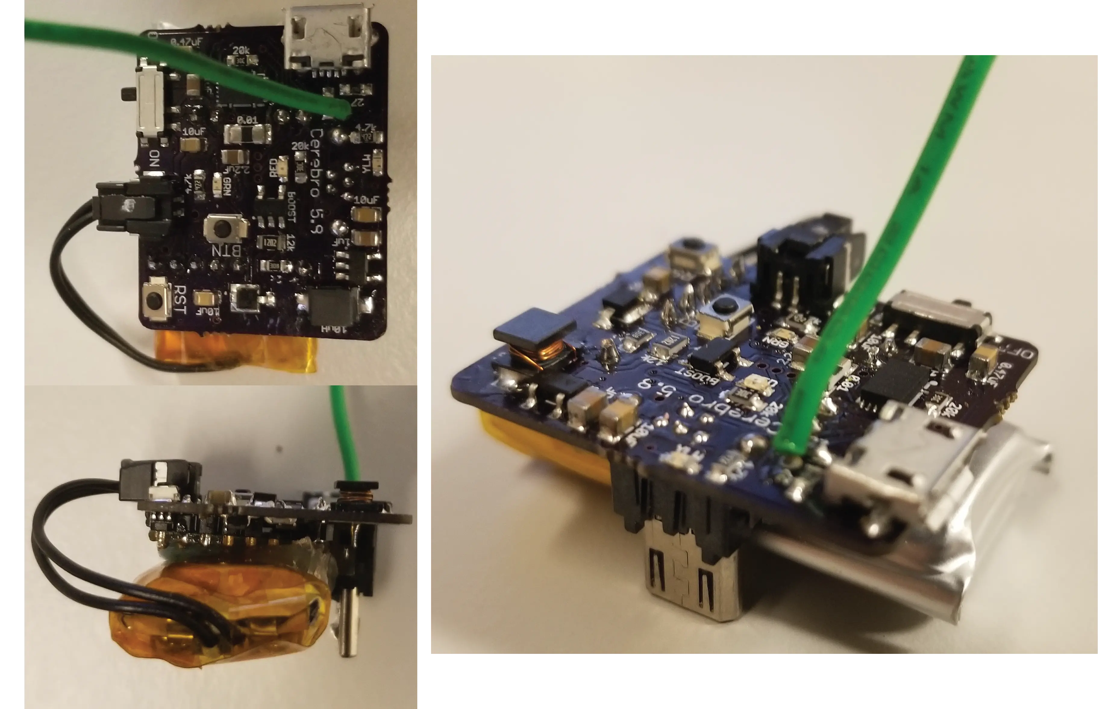
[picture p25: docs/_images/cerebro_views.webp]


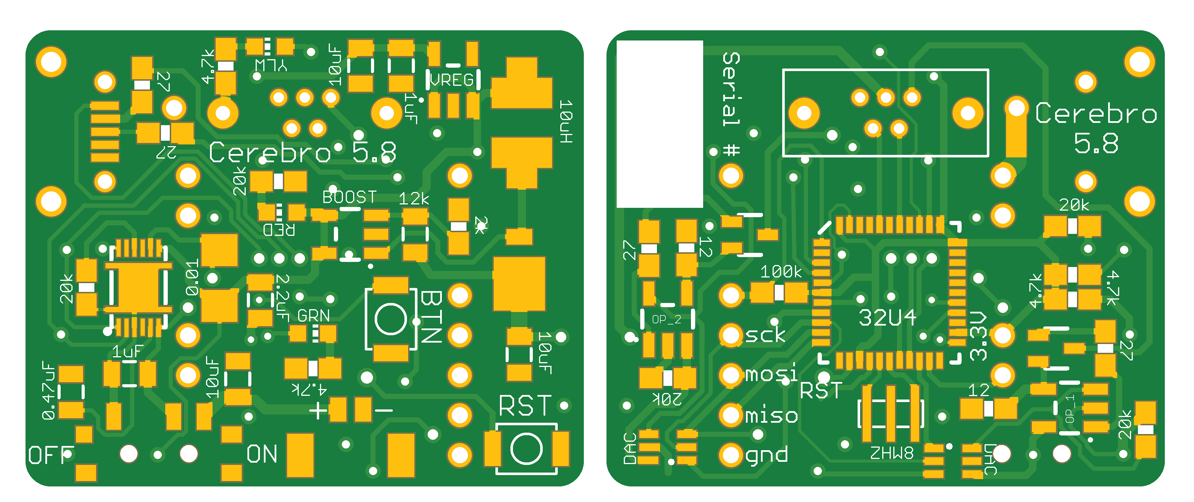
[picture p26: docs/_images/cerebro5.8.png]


Click Here for Design Files (https://github.com/Karpova-Lab/cerebro/tree/master/PCB%20Files/Cerebro%205.8)¶

## Bill of Materials¶

Qty | Description | Part # / Datasheet | Order Link
1 | Cerebro PCB | Cerebro 5.8 | OSH Park (https://oshpark.com/shared_projects/ASxhDBJv)
1 | 550 mAh Battery | 602835 | Amazon (https://www.amazon.com/s?k=B09DPNX4KP)
1 | 915 MHz Radio | RFM69HCW | LowPowerLab (https://lowpowerlab.com/shop/product/158)
1 | Microcontroller | ATMEGA32U4-MUR | Digi-Key (https://www.digikey.com/products/en?keywords=ATMEGA32U4-MURCT-ND)
1 | 8 MHz Resonator | CSTCE8M00G55-R0 | Digi-Key (https://www.digikey.com/products/en?keywords=490-1195-1-ND)
1 | 3.3V Linear Regulator | AP2112K-3.3TRG1 | Digi-Key (https://www.digikey.com/products/en?keywords=%09AP2112K-3.3TRG1DICT-ND)
1 | Fuel Gauge | BQ27441DRZR-G1B | Digi-Key (https://www.digikey.com/product-detail/en/texas-instruments/BQ27441DRZR-G1B/296-39942-1-ND/5177819)
2 | DAC (12-Bit) | LTC2630ACSC6-LZ12#TRMPBF | Digi-Key (https://www.digikey.com/product-detail/en/linear-technology/LTC2630ACSC6-LZ12-TRMPBF/LTC2630ACSC6-LZ12-TRMPBFCT-ND/1643783)
2 | Op Amp | OPA237NA/3K | Digi-Key (https://www.digikey.com/products/en?keywords=296-26265-1-ND)
2 | NPN Transistor | FJX3904TF | Digi-Key (https://www.digikey.com/products/en?keywords=FJX3904TFCT-ND)
1 | Boost Converter | MIC2288YD5-TR | Digi-Key (https://www.digikey.com/products/en?keywords=576-1729-1-ND)
1 | Schottky Diode | MBRM140T3G | Digi-Key (https://www.digikey.com/products/en?keywords=MBRM140T3GOSCT-ND)
1 | 10uH Inductor | LQH43CN100K03L | Digi-Key (https://www.digikey.com/products/en?keywords=490-2519-1-ND)
2 | 2mm Pitch Male Header | M22-2510805 | Digi-Key (https://www.digikey.com/products/en?keywords=952-1992-nd)
1 | Slide Switch | PCM12SMTR | Digi-Key (https://www.digikey.com/products/en?keywords=401-2016-1-nd)
2 | Momentary Button | B3U-1000P | Digi-Key (https://www.digikey.com/products/en?keywords=sw1020ct)
1 | Micro USB vertical plug | ZX20-B-5S-UNIT(30) | Digi-Key (https://www.digikey.com/products/en?keywords=H125237-ND)
1 | Micro USB shielding | ZX20-B-SLDC | Digi-Key (https://www.digikey.com/products/en?keywords=H11496CT-ND)
1 | Micro USB horizontal socket | 10118194-0001LF | Digi-Key (https://www.digikey.com/products/en?keywords=609-4618-1-ND)
1 | Molex Micro-Lock socket | 5055670271 | Digi-Key (https://www.digikey.com/products/en?keywords=WM17038CT-ND)
1 | Molex Micro-Lock plug with wire | 0151360206 | Digi-Key (https://www.digikey.com/products/en?keywords=WM17161-ND)
1 | Red LED (0603) | LTST-C191KRKT | Digi-Key (https://www.digikey.com/products/en?keywords=160-1447-1-ND)
1 | Amber LED (0603) | LNJ437W84RA | Digi-Key (https://www.digikey.com/products/en?keywords=%09LNJ437W84RACT-ND)
1 | Green LED (0603) | SML-D12M8WT86 | Digi-Key (https://www.digikey.com/products/en?keywords=511-1578-1-ND)
1 | 470 nF Capacitor (0805) | | Digi-Key (https://www.digikey.com/product-detail/en/avx-corporation/08055C474KAT2A/478-5033-1-ND/1888244)
2 | 1 μF Capacitor (0805) | | Digi-Key (https://www.digikey.com/products/en?keywords=1276-1066-1-nd)
1 | 2.2 μF Capacitor (0805) | | Digi-Key (https://www.digikey.com/products/en?keywords=587-1286-1)
3 | 10 μF Capacitor (0805) | | Digi-Key (https://www.digikey.com/product-detail/en/murata-electronics-north-america/GRM21BR61E106KA73L/490-5523-1-ND/2334919)
1 | 0.01 Ω Resistor (1206) | | Digi-Key (https://www.digikey.com/products/en?keywords=P0.01BVCT-ND)
2 | 12 Ω Resistor (0603) | | Digi-Key (https://www.digikey.com/products/en?keywords=P12.00BYCT-ND)
4 | 27 Ω Resistor (0603) | | Digi-Key (https://www.digikey.com/products/en?keywords=541-27.0SCT-ND)
1 | 2 kΩ Resistor (0603) | | Digi-Key (https://www.digikey.com/products/en?keywords=RNCP0603FTD2K00CT-ND)
3 | 4.7 kΩ Resistor (0603) | | Digi-Key (https://www.digikey.com/products/en?keywords=311-4.70KHRCT-ND)
2 | 12 kΩ Resistor (0805) | | Digi-Key (https://www.digikey.com/products/en?keywords=311-12.0KCRCT-ND)
5 | 20 kΩ Resistor (0603) | | Digi-Key (https://www.digikey.com/products/en?keywords=RNCP0603FTD20K0CT-ND)
2 | 100 kΩ Resistor (0603) | | Digi-Key (https://www.digikey.com/products/en?keywords=%09311-100KHRCT-ND)

## Programming Instructions¶

### Setup Arduino IDE¶

Follow these instructions : https://learn.adafruit.com/adafruit-feather-32u4-basic-proto/arduino-ide-setup

### Burning a Bootloader¶

Cerebro is designed to be easily reprogrammed through the onboard micro USB. However when builing a Cerebro from scratch, you must first burn a bootloader (https://www.arduino.cc/en/Tutorial/ArduinoISP) onto the microcontroller in order to later upload programs through USB.

To burn a bootloader you need an external programmer that will talk to the microntroller through the In-Circuit Serial Programmer (ISP). You can use an Arduino as your external ISP and temporarily solder wires to the Cerebro PCB. I recommmend using a USB microISP (https://www.tindie.com/products/nsayer/usb-uisp/) along with a Pogo Connector.

1. The programmer needs to connect to the ISP thru-holes (MOSI, MISO, SCK, RST, GND and 3V) on the Cerebro PCB.



2. In the Arduino IDE, select Tools->Board->”Adafruit Feather 32u4”
3. Select Tools->Programmer->”USBtinyISP” or Tools->Programmer->”ArduinoISP” if using an Arduino as the programmer
4. Select Tools->Burn Bootloader

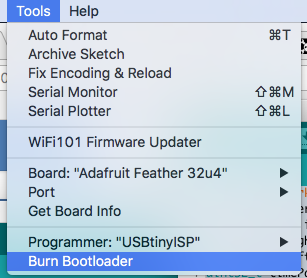
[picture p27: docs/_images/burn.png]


### Uploading Test Program¶

To test that the components on the PCB are soldered correctly and that all of the required connections are being made, we upload a test program.

1. Open testBoard.ino in the Arduino IDE.
2. Select Tools->Board->”Adafruit Feather 32u4”.
3. Under the Tools->Port menu look to see what Serial Ports are available.
4. Connect a battery to Cerebro.
5. Connect Cerebro to your computer with a usb cord and switch on Cerebro. A red LED should be lit, indicating that Cerebro is on.
6. There should now be a new serial port under the Tools->Port menu that wasn’t there in step 2. This is the Cerebro serial port, select it. If there a new serial port didn’t appear in the menu, make sure Cerebro is turned on and connected via USB. If it still doesn’t appear in the menu, the bootloader may have not been burned correctly, so try burning the bootloader again.
7. Click the upload button to upload the the testBoard firmware.
8. Open up Serial Monitor by click the magnifying glass icon.
9. Set the Serial Monitor Baud Rate to 115200 Baud.
10. Two yellow LEDs on Cerebro should be blinking and text should be appearing in the Serial Monitor.
11. Follow the instructions on the Serial Monitor. If everything is working properly then the battery monitor should be able to provide a Battery charge %.

### Uploading Firmware¶

1. Open cerebro.ino in the Arduino IDE.
2. Select Tools->Board->”Adafruit Feather 32u4”.
3. Click the upload button to upload the the Cerebro firmware.

## Assigning a Serial Number¶

A serial number is assigned to each Cerebro. When a Base Station connects to Cerebro, it communicates on the radio channel corresponding to Cerebro’s serial number. This prevents crosstalk between Base Stations and Cerebros in the case where multiple behavior sessions are being run at the same time in the same room. Each Cerebro being used should setup a unique serial number between 1 and 255 using the process below.

1. Start an Xavier session in Debug Mode. The Base Station should be connnected, and have a green check mark.



2. Click Setup New Cerebro



3. Hold down the button labeled “BTN” on Cerebro until the nearby LED blinks twice. A green checkmark should now be next to the “Cerebro Wireless Connection”.

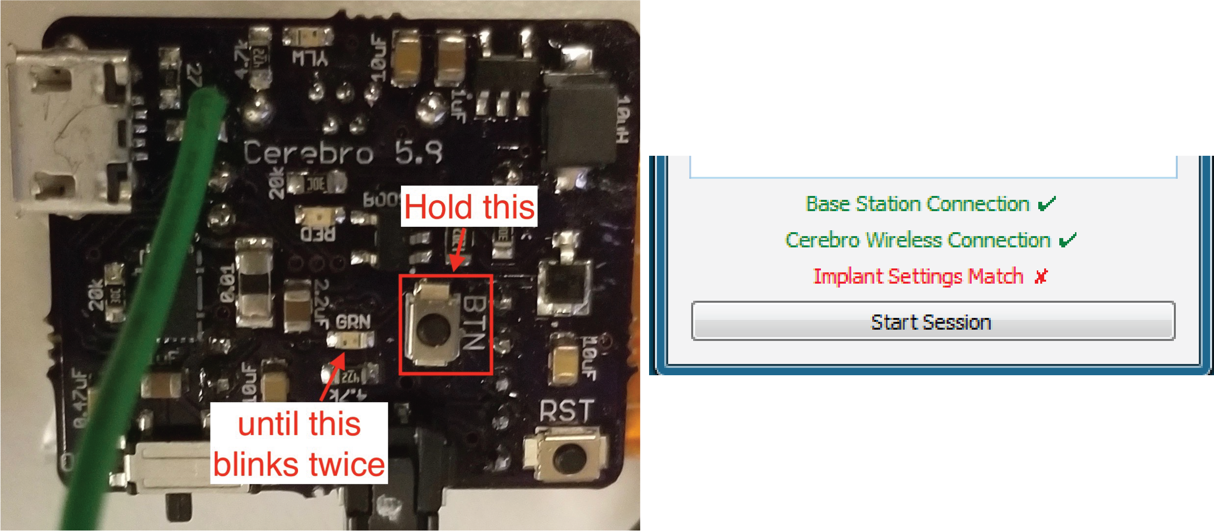
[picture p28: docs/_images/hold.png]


4. Fill in the “Serial Number” box with the serial number you want to give to Cerebro and then click Set Serial Number.



5. After a few seconds, click the Retry Connection button to confirm everything worked. All three indicators should have green check marks. Cerebro now has a serial number saved to its memory, and whenever it is turned on it will try to communicate with a Base Station on a radio channel of the same number.



Next Previous

© Copyright 2015-2022, Andy Lustig Last updated on Jun 13, 2022.

Built with Sphinx (http://sphinx-doc.org/) using a theme (https://github.com/rtfd/sphinx_rtd_theme) provided by Read the Docs (https://readthedocs.org).

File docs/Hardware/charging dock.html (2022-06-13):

- Docs »
- Charging Dock
- Cerebro on GitHub (https://github.com/Karpova-Lab/cerebro)

Next Previous

# Charging Dock¶





Click Here for Design Files (https://github.com/Karpova-Lab/cerebro/tree/master/PCB%20Files/Charging%20Dock%202.1)¶

## Bill of Materials¶

Qty | Description | Datasheet | Order Link
1 | Charging Dock PCB | Charging Dock 2.0 | OSH Park (https://oshpark.com/shared_projects/hz6upCEq)
1 | Molex Micro-Lock socket | 5055670271 | Digi-Key (https://www.digikey.com/products/en?keywords=WM17038CT-ND)
6 | Lipoly Charging IC | MCP73831T-2ACI/OT | Digi-Key (https://www.digikey.com/products/en?keywords=%09MCP73831T-2ACI%2FOTCT-ND)
1 | DC Barrel Power Jack | PJ-037A | Digi-Key (https://www.digikey.com/products/en?keywords=cp-037a-nd)
1 | 5V 2.5A Power Supply | SWI12-5-N-P5R | Digi-Key (https://www.digikey.com/product-detail/en/cui-inc/SWI12-5-N-P5R/102-3425-ND/5287234)
6 | Green LED | 151031VS06000 | Digi-Key (https://www.digikey.com/products/en?keywords=732-5008-ND)
6 | Red LED | 151031SS06000 | Digi-Key (https://www.digikey.com/products/en?keywords=732-5006-ND)
12 | 0805 470 Ω Resistor
6 | 0805 2.5 KΩ Resistor
12 | 0805 10 μF Capacitor

Next Previous

© Copyright 2015-2022, Andy Lustig Last updated on Jun 13, 2022.

Built with Sphinx (http://sphinx-doc.org/) using a theme (https://github.com/rtfd/sphinx_rtd_theme) provided by Read the Docs (https://readthedocs.org).

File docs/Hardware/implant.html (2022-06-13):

- Docs »
- Head Implant
- Cerebro on GitHub (https://github.com/Karpova-Lab/cerebro)

Next Previous

# Head Implant¶





Click Here for Design Files (https://github.com/Karpova-Lab/cerebro/tree/master/PCB%20Files/Implant%205.3)¶

## Required Tools¶

- Ruler
- Soldering iron
- Tweezers
- Fiber gripper (https://www.thorlabschina.cn/thorproduct.cfm?partnumber=BFG1)
- Fiber stripper (https://www.thorlabs.com/thorProduct.cfm?partNumber=T12S21)
- Fiber cleaver (http://www.fiberinstrumentsales.com/fis-lynx-precision-cleaver-with-fiber-basket.html)
- 3-axis fiber launch system (http://www.thorlabs.com/thorproduct.cfm?partnumber=MBT612D/M)
- Power meter (https://www.thorlabs.com/thorproduct.cfm?partnumber=PM121D) and photodiode sensor (https://www.thorlabs.com/thorproduct.cfm?partnumber=S121C)
- Adjustable DC Power Supply (https://www.amazon.com/KORAD-KD3005D-Precision-Adjustable-Regulated/dp/B00FPU6G4E?s=hi&dpID=41CeDR0WTPL&preST=_SY300_QL70_&dpSrc=srch)
- Ultraviolet light (https://www.amazon.com/TaoTronics-TT-FL001-Flashlight-Blacklight-Ultraviolet/dp/B00RV8PREI)

## Bill of Materials¶

Qty | Description | Datasheet | Order Link
1 | Implant PCB | Implant 5.3 | OSH Park (https://oshpark.com/shared_projects/k8Ikpli6)
1 | Laser Diode | PLT5 520_B1_2_3 | World Star Tech (http://www.worldstartech.com/products/laser-diodes/green-laser-diode-osram/)
1 | Fiber | F-MBB | Newport (https://www.newport.com/p/F-MBB)
1 | UV curing adhesive | NOA 68 | Norland Products (https://www.norlandproducts2.com/adhesives/adproductsdetail_header_removed.asp?Prdid=68)
1 | Ferrule | MM-FER2007C | Precision Fiber Products (https://precisionfiberproducts.com/pfp-lc-1-25mm-od-multimode-ceramic-zirconia-ferrules/)
1 | Epoxy | T120023C | Fiber Instrument Sales (http://www.fiberinstrumentsales.com/fis-room-cure-epoxy-2-grams.html)
2 | Micro USB vertical socket | 1051330011 | Digi-Key (https://www.digikey.com/products/en?keywords=WM10134CT-ND)
2 | Heat shrink tubing | HSTTV12-Y | Digi-Key (https://www.digikey.com/products/en?x=0&y=0&lang=en&site=us&keywords=298-11559-ND)
2 | 0603 10 kΩ Resistor
1 | 0603 20 kΩ Resistor

## Assembly Instructions¶

### Prepare Fiber¶

1. Tape down the fiber
2. Use a fiber stripper to remove the outer blue jacket from the fiber



3. Using a fiber cleaver, cut off the end of fiber to make a clean tip
4. Continue cutting the fiber into ~16mm pieces

### Align Fiber¶

1. Insert laser diode into connector
2. Place connector in alignment jig
3. Place fiber in alignment jig
4. Turn on the power meter and connect to computer over usb
5. Open up the Thorlabs’ Power Meter Software (https://www.thorlabs.com/software_pages/ViewSoftwarePage.cfm?Code=PM100x)
6. Establish the USB connection with Power meter by selecting the device and clicking “OK”



7. Adjust the following settings:
- Range: 12mW
- Wave: 520nm
- Log Configuration
  - No of Samples: 20,000
  - Interval Time: 0.1



8. Click Start Log



9. Set the power supply to 8.0 volts with a current limit of 300 mA
10. Provide power to the laser diode by pressing the “on/off” button
11. While watching the power graph update, use the 3-axis fiber launch system (http://www.thorlabs.com/thorproduct.cfm?partnumber=MBT612D/M) to adjust the x, y, and z alignment of the fiber with respect to the laser diode.
12. When you are happy with the alignment, apply UV curing adhesive to the fiber/laserdiode junction.
13. Cure the adhesive using UV light

### Fiber Guide Construction¶

A fiber guide is needed to ensure that the fibers are at a precise distance apart, and are parallel. The distance will depend on what area of the brain is being targeted. Below are files for 1.5 mm and 2.74 mm gap between fibers.

- Fiber guide_1,5mm gap.dxf
- Fiber guide_1,5mm gap.ai
- Fiber guide_2,74mm gap.ai

The laser cutter speed and power settings may need to be tweaked to get a good fit for the the ceramic ferrules.

1. Insert the ceramic ferrules into the acrylic fiber guide. The flat side of the ferrules should be flush with the face of the acrylic.



### Combine PCB, Laser Diodes, and Fiber Guide¶

1. Solder the vertical microusb connector onto the PCB
2. Solder 1 leg of each laser diode onto the PCB
3. Bend the laser diodes toward eachother so the tips of the fiber slightly intersect near their tips
4. Solder the remaining legs of the laser diodes
5. Cut ~10mm of heat shrink tubing and slide it onto one of the laser diodes
6. Apply heat to the heat shrink tubing

Warning

Heat can weaken the UV glue that is used to attach the fiber. Be careful not to apply too much heat for too long as you may risk weakening the glue, causing the fiber to move out of alignment or detach completely.

7. Slide the fiber guide onto the two fibers. Adjust the
8. Surround the fibers and laser diodes with epoxy
9. Place heatshrink tubing around the clear epoxy section of the implant
10. Place and solder the remaining resistors onto the PCB

Next Previous

© Copyright 2015-2022, Andy Lustig Last updated on Jun 13, 2022.

Built with Sphinx (http://sphinx-doc.org/) using a theme (https://github.com/rtfd/sphinx_rtd_theme) provided by Read the Docs (https://readthedocs.org).

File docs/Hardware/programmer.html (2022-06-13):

- Docs »
- Pogo Connector
- Cerebro on GitHub (https://github.com/Karpova-Lab/cerebro)

Next Previous

# Pogo Connector¶





Click Here for Design Files (https://github.com/Karpova-Lab/cerebro/tree/master/PCB%20Files/Cerebro%20ICSP%201.2)¶

## Bill of Materials¶

Qty | Description | Datasheet | Order Link
2 | Programmer PCB | Cerebro ICSP 1.2 | OSH Park (https://oshpark.com/shared_projects/PXMM4F8R)
1 | 6 Pin Socket | 75869-331LF | Digi-Key (https://www.digikey.com/products/en?keywords=609-5122-ND)
5 | Spear Head Pogo Pin | 394 | Adafruit (https://www.adafruit.com/product/394)
1 | Needle Head Pogo Pin | 2430 | Adafruit (https://www.adafruit.com/product/2430)
3 | M3 x 0.5 Screw | 92492A717 | McMaster-Carr (https://www.mcmaster.com/#92492A717)
3 | Nylon Spacer | 93657A203 | McMaster-Carr (https://www.mcmaster.com/#93657A203)
3 | M3 Nut | 90695A033 | McMaster-Carr (https://www.mcmaster.com/#90695A033)

Use the Pogo connector to burn a bootloader onto Cerebro

Next Previous

© Copyright 2015-2022, Andy Lustig Last updated on Jun 13, 2022.

Built with Sphinx (http://sphinx-doc.org/) using a theme (https://github.com/rtfd/sphinx_rtd_theme) provided by Read the Docs (https://readthedocs.org).

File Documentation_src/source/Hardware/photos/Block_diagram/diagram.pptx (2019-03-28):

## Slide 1

Base Station

Cerebro

LiPo Battery

Battery Monitor

Serial Communication

Micro USB
Socket

RJ45
Jack

or

MCU

Radio

Radio

MCU

TTL
signal

Current Control

Voltage Booster

Micro USB
Plug

Brain

Micro USB
Socket

Head Implant

Laser
Diodes

Digital Communication

Power

Optical
Fibers

Light

Phototransistor Feedback

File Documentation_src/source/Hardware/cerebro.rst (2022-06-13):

:github_url: https://github.com/Karpova-Lab/cerebro

=======
Cerebro 
=======

.. include:: Characters/isogrk1.txt
.. include:: Characters/mmlalias.txt





  `Click Here for Design Files <https://github.com/Karpova-Lab/cerebro/tree/master/PCB%20Files/Cerebro%205.8>`_ 

Bill of Materials
=================
+-----+---------------------------------+-------------------------------------------------------------------+---------------------------------------------------------------------------------------------------------------------------------------------------+
| Qty | Description                     | Part # / Datasheet                                                | Order Link                                                                                                                                        | 
+=====+=================================+===================================================================+===================================================================================================================================================+
| 1   | Cerebro PCB                     |  :download:`Cerebro 5.8<Datasheets/cerebro5.8.pdf>`               | `OSH Park <https://oshpark.com/shared_projects/ASxhDBJv>`__                                                                                       | 
+-----+---------------------------------+-------------------------------------------------------------------+---------------------------------------------------------------------------------------------------------------------------------------------------+
| 1   | 550 mAh Battery                 |  602835                                                           | `Amazon <https://www.amazon.com/s?k=B09DPNX4KP>`__                                                                                                |  
+-----+---------------------------------+-------------------------------------------------------------------+---------------------------------------------------------------------------------------------------------------------------------------------------+
| 1   | 915 MHz Radio                   |  :download:`RFM69HCW<Datasheets/radio.pdf>`                       | `LowPowerLab <https://lowpowerlab.com/shop/product/158>`__                                                                                        | 
+-----+---------------------------------+-------------------------------------------------------------------+---------------------------------------------------------------------------------------------------------------------------------------------------+
| 1   | Microcontroller                 |  :download:`ATMEGA32U4-MUR<Datasheets/MCU_32u4.pdf>`              | `Digi-Key <https://www.digikey.com/products/en?keywords=ATMEGA32U4-MURCT-ND>`__                                                                   | 
+-----+---------------------------------+-------------------------------------------------------------------+---------------------------------------------------------------------------------------------------------------------------------------------------+
| 1   | 8 MHz Resonator                 |  :download:`CSTCE8M00G55-R0<Datasheets/resonator_8mhz.pdf>`       | `Digi-Key <https://www.digikey.com/products/en?keywords=490-1195-1-ND>`__                                                                         | 
+-----+---------------------------------+-------------------------------------------------------------------+---------------------------------------------------------------------------------------------------------------------------------------------------+
| 1   | 3.3V Linear Regulator           |  :download:`AP2112K-3.3TRG1<Datasheets/regulator_3v_linear.pdf>`  | `Digi-Key <https://www.digikey.com/products/en?keywords=%09AP2112K-3.3TRG1DICT-ND>`__                                                             | 
+-----+---------------------------------+-------------------------------------------------------------------+---------------------------------------------------------------------------------------------------------------------------------------------------+
| 1   | Fuel Gauge                      |  :download:`BQ27441DRZR-G1B<Datasheets/fuel_gauge.pdf>`           | `Digi-Key <https://www.digikey.com/product-detail/en/texas-instruments/BQ27441DRZR-G1B/296-39942-1-ND/5177819>`__                                 | 
+-----+---------------------------------+-------------------------------------------------------------------+---------------------------------------------------------------------------------------------------------------------------------------------------+
| 2   | DAC (12-Bit)                    |  :download:`LTC2630ACSC6-LZ12#TRMPBF<Datasheets/DAC.pdf>`         | `Digi-Key <https://www.digikey.com/product-detail/en/linear-technology/LTC2630ACSC6-LZ12-TRMPBF/LTC2630ACSC6-LZ12-TRMPBFCT-ND/1643783>`__         | 
+-----+---------------------------------+-------------------------------------------------------------------+---------------------------------------------------------------------------------------------------------------------------------------------------+
| 2   | Op Amp                          |  :download:`OPA237NA/3K<Datasheets/opamp.pdf>`                    | `Digi-Key <https://www.digikey.com/products/en?keywords=296-26265-1-ND>`__                                                                        | 
+-----+---------------------------------+-------------------------------------------------------------------+---------------------------------------------------------------------------------------------------------------------------------------------------+
| 2   | NPN Transistor                  |  :download:`FJX3904TF<Datasheets/npn_transistor.pdf>`             | `Digi-Key <https://www.digikey.com/products/en?keywords=FJX3904TFCT-ND>`__                                                                        | 
+-----+---------------------------------+-------------------------------------------------------------------+---------------------------------------------------------------------------------------------------------------------------------------------------+
| 1   | Boost Converter                 |  :download:`MIC2288YD5-TR<Datasheets/boost_converter.pdf>`        | `Digi-Key <https://www.digikey.com/products/en?keywords=576-1729-1-ND>`__                                                                         | 
+-----+---------------------------------+-------------------------------------------------------------------+---------------------------------------------------------------------------------------------------------------------------------------------------+
| 1   | Schottky Diode                  |  :download:`MBRM140T3G<Datasheets/schottky.pdf>`                  | `Digi-Key <https://www.digikey.com/products/en?keywords=MBRM140T3GOSCT-ND>`__                                                                     | 
+-----+---------------------------------+-------------------------------------------------------------------+---------------------------------------------------------------------------------------------------------------------------------------------------+
| 1   | 10uH Inductor                   |  :download:`LQH43CN100K03L<Datasheets/inductor.pdf>`              | `Digi-Key <https://www.digikey.com/products/en?keywords=490-2519-1-ND>`__                                                                         | 
+-----+---------------------------------+-------------------------------------------------------------------+---------------------------------------------------------------------------------------------------------------------------------------------------+
| 2   | 2mm Pitch Male Header           |  :download:`M22-2510805<Datasheets/header_male_2mm.pdf>`          | `Digi-Key <https://www.digikey.com/products/en?keywords=952-1992-nd>`__                                                                           | 
+-----+---------------------------------+-------------------------------------------------------------------+---------------------------------------------------------------------------------------------------------------------------------------------------+
| 1   | Slide Switch                    |  :download:`PCM12SMTR<Datasheets/slide_switch2.pdf>`              | `Digi-Key <https://www.digikey.com/products/en?keywords=401-2016-1-nd>`__                                                                         | 
+-----+---------------------------------+-------------------------------------------------------------------+---------------------------------------------------------------------------------------------------------------------------------------------------+
| 2   | Momentary Button                |  :download:`B3U-1000P<Datasheets/momentary.pdf>`                  | `Digi-Key <https://www.digikey.com/products/en?keywords=sw1020ct>`__                                                                              | 
+-----+---------------------------------+-------------------------------------------------------------------+---------------------------------------------------------------------------------------------------------------------------------------------------+
| 1   | Micro USB vertical plug         |  :download:`ZX20-B-5S-UNIT(30)<Datasheets/usb_plug_vertical.pdf>` | `Digi-Key <https://www.digikey.com/products/en?keywords=H125237-ND>`__                                                                            | 
+-----+---------------------------------+-------------------------------------------------------------------+---------------------------------------------------------------------------------------------------------------------------------------------------+
| 1   | Micro USB shielding             |  :download:`ZX20-B-SLDC<Datasheets/usb_shielding.pdf>`            | `Digi-Key <https://www.digikey.com/products/en?keywords=H11496CT-ND>`__                                                                           | 
+-----+---------------------------------+-------------------------------------------------------------------+---------------------------------------------------------------------------------------------------------------------------------------------------+
| 1   | Micro USB horizontal socket     |  :download:`10118194-0001LF<Datasheets/usb_plug_horizontal.pdf>`  | `Digi-Key <https://www.digikey.com/products/en?keywords=609-4618-1-ND>`__                                                                         | 
+-----+---------------------------------+-------------------------------------------------------------------+---------------------------------------------------------------------------------------------------------------------------------------------------+
| 1   | Molex Micro-Lock socket         |  :download:`5055670271<Datasheets/microlock_socket.pdf>`          | `Digi-Key <https://www.digikey.com/products/en?keywords=WM17038CT-ND>`__                                                                          | 
+-----+---------------------------------+-------------------------------------------------------------------+---------------------------------------------------------------------------------------------------------------------------------------------------+
| 1   | Molex Micro-Lock plug with wire |  :download:`0151360206<Datasheets/microlock_plug.pdf>`            | `Digi-Key <https://www.digikey.com/products/en?keywords=WM17161-ND>`__                                                                            | 
+-----+---------------------------------+-------------------------------------------------------------------+---------------------------------------------------------------------------------------------------------------------------------------------------+
| 1   | Red LED (0603)                  |  :download:`LTST-C191KRKT<Datasheets/led_red.pdf>`                | `Digi-Key <https://www.digikey.com/products/en?keywords=160-1447-1-ND>`__                                                                         | 
+-----+---------------------------------+-------------------------------------------------------------------+---------------------------------------------------------------------------------------------------------------------------------------------------+
| 1   | Amber LED (0603)                |  :download:`LNJ437W84RA<Datasheets/led_amber.pdf>`                | `Digi-Key <https://www.digikey.com/products/en?keywords=%09LNJ437W84RACT-ND>`__                                                                   | 
+-----+---------------------------------+-------------------------------------------------------------------+---------------------------------------------------------------------------------------------------------------------------------------------------+
| 1   | Green LED (0603)                |  :download:`SML-D12M8WT86<Datasheets/led_green.pdf>`              | `Digi-Key <https://www.digikey.com/products/en?keywords=511-1578-1-ND>`__                                                                         | 
+-----+---------------------------------+-------------------------------------------------------------------+---------------------------------------------------------------------------------------------------------------------------------------------------+
| 1   | 470 nF Capacitor (0805)         |                                                                   | `Digi-Key <https://www.digikey.com/product-detail/en/avx-corporation/08055C474KAT2A/478-5033-1-ND/1888244>`__                                     | 
+-----+---------------------------------+-------------------------------------------------------------------+---------------------------------------------------------------------------------------------------------------------------------------------------+
| 2   | 1 |mgr|\F Capacitor (0805)      |                                                                   | `Digi-Key <https://www.digikey.com/products/en?keywords=1276-1066-1-nd>`__                                                                        | 
+-----+---------------------------------+-------------------------------------------------------------------+---------------------------------------------------------------------------------------------------------------------------------------------------+
| 1   | 2.2 |mgr|\F Capacitor (0805)    |                                                                   | `Digi-Key <https://www.digikey.com/products/en?keywords=587-1286-1>`__                                                                            | 
+-----+---------------------------------+-------------------------------------------------------------------+---------------------------------------------------------------------------------------------------------------------------------------------------+
| 3   | 10 |mgr|\F Capacitor (0805)     |                                                                   | `Digi-Key <https://www.digikey.com/product-detail/en/murata-electronics-north-america/GRM21BR61E106KA73L/490-5523-1-ND/2334919>`__                | 
+-----+---------------------------------+-------------------------------------------------------------------+---------------------------------------------------------------------------------------------------------------------------------------------------+
| 1   | 0.01 |OHgr| Resistor (1206)     |                                                                   | `Digi-Key <https://www.digikey.com/products/en?keywords=P0.01BVCT-ND>`__                                                                          | 
+-----+---------------------------------+-------------------------------------------------------------------+---------------------------------------------------------------------------------------------------------------------------------------------------+
| 2   | 12 |OHgr| Resistor (0603)       |                                                                   | `Digi-Key <https://www.digikey.com/products/en?keywords=P12.00BYCT-ND>`__                                                                         | 
+-----+---------------------------------+-------------------------------------------------------------------+---------------------------------------------------------------------------------------------------------------------------------------------------+
| 4   | 27 |OHgr| Resistor (0603)       |                                                                   | `Digi-Key <https://www.digikey.com/products/en?keywords=541-27.0SCT-ND>`__                                                                        | 
+-----+---------------------------------+-------------------------------------------------------------------+---------------------------------------------------------------------------------------------------------------------------------------------------+
| 1   | 2 k\ |OHgr| Resistor (0603)     |                                                                   | `Digi-Key <https://www.digikey.com/products/en?keywords=RNCP0603FTD2K00CT-ND>`__                                                                  | 
+-----+---------------------------------+-------------------------------------------------------------------+---------------------------------------------------------------------------------------------------------------------------------------------------+
| 3   | 4.7 k\ |OHgr| Resistor (0603)   |                                                                   | `Digi-Key <https://www.digikey.com/products/en?keywords=311-4.70KHRCT-ND>`__                                                                      | 
+-----+---------------------------------+-------------------------------------------------------------------+---------------------------------------------------------------------------------------------------------------------------------------------------+
| 2   | 12 k\ |OHgr| Resistor (0805)    |                                                                   | `Digi-Key <https://www.digikey.com/products/en?keywords=311-12.0KCRCT-ND>`__                                                                      | 
+-----+---------------------------------+-------------------------------------------------------------------+---------------------------------------------------------------------------------------------------------------------------------------------------+
| 5   | 20 k\ |OHgr| Resistor (0603)    |                                                                   | `Digi-Key <https://www.digikey.com/products/en?keywords=RNCP0603FTD20K0CT-ND>`__                                                                  | 
+-----+---------------------------------+-------------------------------------------------------------------+---------------------------------------------------------------------------------------------------------------------------------------------------+
| 2   | 100 k\ |OHgr| Resistor (0603)   |                                                                   | `Digi-Key <https://www.digikey.com/products/en?keywords=%09311-100KHRCT-ND>`__                                                                    | 
+-----+---------------------------------+-------------------------------------------------------------------+---------------------------------------------------------------------------------------------------------------------------------------------------+

Programming Instructions
========================

.. _burn boot:

Setup Arduino IDE
-----------------
Follow these instructions : https://learn.adafruit.com/adafruit-feather-32u4-basic-proto/arduino-ide-setup

Burning a Bootloader
--------------------

Cerebro is designed to be easily reprogrammed through the onboard micro USB. 
However when builing a Cerebro from scratch, you must first burn a `bootloader <https://www.arduino.cc/en/Tutorial/ArduinoISP>`_  onto the microcontroller in order to later upload programs through USB. 

To burn a bootloader you need an external programmer that will talk to the microntroller through the In-Circuit Serial Programmer (ISP). 
You can use an Arduino as your external ISP and temporarily solder wires to the Cerebro PCB. 
I recommmend using a `USB microISP <https://www.tindie.com/products/nsayer/usb-uisp/>`_ along with a :doc:`Pogo Connector <programmer>`.

1. The programmer needs to connect to the ISP thru-holes (MOSI, MISO, SCK, RST, GND and 3V) on the Cerebro PCB.



2. In the Arduino IDE, select Tools->Board->"Adafruit Feather 32u4" 
3. Select  Tools->Programmer->"USBtinyISP" or Tools->Programmer->"ArduinoISP" if using an Arduino as the programmer
4. Select Tools->Burn Bootloader



Uploading Test Program
----------------------
To test that the components on the PCB are soldered correctly and that all of the required connections are being made, we upload a test program. 

1. Open testBoard.ino in the Arduino IDE.
2. Select Tools->Board->"Adafruit Feather 32u4".
3. Under the Tools->Port menu look to see what Serial Ports are available. 
4. Connect a battery to Cerebro.
5. Connect Cerebro to your computer with a usb cord and switch on Cerebro. A red LED should be lit, indicating that Cerebro is on.
6. There should now be a new serial port under the Tools->Port menu that wasn't there in step 2. This is the Cerebro serial port, select it. If there a new serial port didn't appear in the menu, make sure Cerebro is turned on and connected via USB. If it still doesn't appear in the menu, the bootloader may have not been burned correctly, so try burning the bootloader again.
7. Click the upload button to upload the the testBoard firmware.
8. Open up Serial Monitor by click the magnifying glass icon.
9. Set the Serial Monitor Baud Rate to 115200 Baud.
10. Two yellow LEDs on Cerebro should be blinking and text should be appearing in the Serial Monitor.
11. Follow the instructions on the Serial Monitor. If everything is working properly then the battery monitor should be able to provide a Battery charge %.

Uploading Firmware
------------------
1. Open cerebro.ino in the Arduino IDE.
2. Select Tools->Board->"Adafruit Feather 32u4".
3. Click the upload button to upload the the Cerebro firmware.

Assigning a Serial Number
=========================
A serial number is assigned to each Cerebro. When a Base Station connects to Cerebro, it communicates on the radio channel corresponding to Cerebro's serial number. This prevents crosstalk between Base Stations and Cerebros in the case where multiple behavior sessions are being run at the same time in the same room. Each Cerebro being used should setup a unique serial number between 1 and 255 using the process below. 

1. Start an Xavier session in Debug Mode. The Base Station should be connnected, and have a green check mark.



2. Click ``Setup New Cerebro`` 



3. Hold down the button labeled "BTN" on Cerebro until the nearby LED blinks twice. A green checkmark should now be next to the "Cerebro Wireless Connection".



4. Fill in the "Serial Number" box with the serial number you want to give to Cerebro and then click ``Set Serial Number``.



5. After a few seconds, click the ``Retry Connection`` button to confirm everything worked. All three indicators should have green check marks. Cerebro now has a serial number saved to its memory, and whenever it is turned on it will try to communicate with a Base Station on a radio channel of the same number.



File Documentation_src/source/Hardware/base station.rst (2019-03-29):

:github_url: https://github.com/Karpova-Lab/cerebro

============
Base Station
============

.. include:: Characters/isogrk1.txt





  `Click Here for Design Files <https://github.com/Karpova-Lab/cerebro/tree/master/PCB%20Files/Base%20Station%202.5>`_ 

Bill of Materials
=================

+-----+-----------------------------+-----------------------------------------------------------------------+------------------------------------------------------------------------------------+
| Qty | Description                 | Datasheet                                                             | Order Link                                                                         | 
+=====+=============================+=======================================================================+====================================================================================+
| 1   | Base Station PCB            |  :download:`Base Station 2.5<Datasheets/base_station_2.5.pdf>`        | `OSH Park <https://oshpark.com/shared_projects/qpPpopqr>`__                        | 
+-----+-----------------------------+-----------------------------------------------------------------------+------------------------------------------------------------------------------------+
| 1   | Feather 32u4 RFM69HCW       |  :download:`3076<Datasheets/feather_radio.pdf>`                       | `Digi-Key <https://www.digikey.com/products/en?keywords=1528-1663-ND>`__           | 
+-----+-----------------------------+-----------------------------------------------------------------------+------------------------------------------------------------------------------------+
| 1   | USB to Serial Converter     |  :download:`CY7C65213-28PVXI<Datasheets/usb_to_serial_converter.pdf>` | `Digi-Key <https://www.digikey.com/products/en?keywords=%09CY7C65213-28PVXI-ND>`__ | 
+-----+-----------------------------+-----------------------------------------------------------------------+------------------------------------------------------------------------------------+
| 1   | Voltage Level Translator    |  :download:`TXB0104PWR<Datasheets/voltage_translator.pdf>`            | `Digi-Key <https://www.digikey.com/products/en?keywords=296-21929-1-nd>`__         | 
+-----+-----------------------------+-----------------------------------------------------------------------+------------------------------------------------------------------------------------+
| 1   | Micro USB horizontal socket |  :download:`10118194-0001LF<Datasheets/usb_plug_horizontal.pdf>`      | `Digi-Key <https://www.digikey.com/products/en?keywords=609-4618-1-ND>`__          | 
+-----+-----------------------------+-----------------------------------------------------------------------+------------------------------------------------------------------------------------+
| 1   | Antenna                     |  :download:`HA.31.A<Datasheets/antenna_base.pdf>`                     | `Digi-Key <https://www.digikey.com/products/en?keywords=931-1452>`__               | 
+-----+-----------------------------+-----------------------------------------------------------------------+------------------------------------------------------------------------------------+
| 2   | 0805 51 k\ |OHgr| Resistor  |                                                                       |                                                                                    | 
+-----+-----------------------------+-----------------------------------------------------------------------+------------------------------------------------------------------------------------+

Downloads
=================
- `Cypress USB Driver <http://www.cypress.com/documentation/software-and-drivers/usb-serial-software-development-kit>`_ 
- `Adafruit Feather Driver <https://learn.adafruit.com/adafruit-feather-32u4-basic-proto/using-with-arduino-ide>`_

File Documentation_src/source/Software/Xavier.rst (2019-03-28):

:github_url: https://github.com/Karpova-Lab/cerebro

======
Xavier
======



Installation
===================

System Requirements
-------------------
  - Windows XP or newer

  .. _setup default:

Download Instructions
---------------------
1. Download and install the `USB-Serial Windows Driver Installer <http://www.cypress.com/documentation/software-and-drivers/usb-serial-software-development-kit>`_ 
2. Download and unzip :download:`Xavier Deployment Folder<Deployment.zip>`
3. Open up Xavier.exe



4. Setup a :ref:`default directory<edit default directory>` that data will be saved to.

Settings
========
Access Xavier Settings by navigating to **File->Settings..** or by pressing :kbd:`Ctrl` + :kbd:`,`



.. note::
  Settings cannot be changed in the middle of a session

.. _edit default directory:

Edit Default Save Directory
-------------------------------

1.  Click ``Change Directory`` to setup a new save location.



2. Navigate to an existing folder or create a new folder for future data.



3. Finally, click **Select Folder**. The "Current Directory" will reflect updated save path





.. _add items:

Edit Session Setup Lists
------------------------
Adding Items
````````````
Type new items into the textboxes and click ``Add Item`` (or press :kbd:`Enter`)



Removing Items
``````````````
Select the item from list you want to remove and click ``Remove Selected``



.. _label ports:

Labeling COM Ports
------------------
When multiple usb devices are connected to the computer, it can be hard to keep track of which COM Port belongs to which device. To minimize confusion when connecting
to serial ports, Xavier allows you to label COM Ports.



1. Double-click the labeled COM Port from the list that you want to edit. A label editing dialog will appear.
2. Type the new label into the textbox and click ``Change Label``.



Running an Experiment
=====================

.. _start session:

Session Setup
-------------
1. Fill out experimental setup information.



.. note::
  The rig and rat lists can be :ref:`edited <add items>`

2. Select a Base Station Serial Port.



.. note::  
  The COM port drowdown list can be :ref:`labeled<label ports>`

3. Click ``Connect to Base Station``.



4. A startup sequence dialog box will appear. Xavier will try to establish a connection between Base Station and Cerebro. Once connected, Xavier will make sure that the laser diode power settings on Cerebro match laser diode powers for the rat/implant that was selected in step 1. If there are red X's, make sure the correct Serial Port was selected, make sure Cerebro has been turned on, and then click ``Retry``.



5. If everything on the list has green checkmarks, click ``Start Session`` to begin the session. 



.. _waveform parameters:

Edit Waveform Parameters
------------------------
Five waveform parameters (Start Delay, On Time, Off Time, Train Duration, Ramp Down) can be wirelessly changed throughout the session.
The user can make changes using either a **Single Shot** mode with an optional ramp down or **Pulse Train** mode. Non-applicable 
parameters are automatically set to zero depending on the options selected.



1. Check the Cerebro Status to determine whether the waveform parameters are set as you wish.



2. If you would like to modify the parameters, select "Single Shot" or "Pulse Train", then modify the parameters in the "Waveform Parameters" section.



3. Click ``Send New Waveform Parameters``.

Ending a Session and Saving Data
--------------------------------

1. When you are ready to end the session click ``Save Session``.

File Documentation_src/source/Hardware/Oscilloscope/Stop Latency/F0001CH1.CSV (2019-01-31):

Record Length | 2.500000e+03 | -0.002200000000 | 3.40000
Sample Interval | 2.000000e-05 | -0.002180000000 | 3.40000
Trigger Point | 1.100000000000e+02 | -0.002160000000 | 3.40000
 |  | -0.002140000000 | 3.40000
 |  | -0.002120000000 | 3.40000
 |  | -0.002100000000 | 3.40000
Source | CH1 | -0.002080000000 | 3.40000
Vertical Units | V | -0.002060000000 | 3.40000
Vertical Scale | 5.000000e+00 | -0.002040000000 | 3.40000
Vertical Offset | -1.780000e+01 | -0.002020000000 | 3.40000
Horizontal Units | s | -0.002000000000 | 3.40000
Horizontal Scale | 5.000000e-03 | -0.001980000000 | 3.40000
Pt Fmt | Y | -0.001960000000 | 3.40000
Yzero | 0.000000e+00 | -0.001940000000 | 3.40000
Probe Atten | 1.000000e+00 | -0.001920000000 | 3.40000
Model Number | TDS2012B | -0.001900000000 | 3.40000
Serial Number | C062163 | -0.001880000000 | 3.40000
Firmware Version | FV:v22.16 | -0.001860000000 | 3.40000
 |  | -00.001840000000 | 3.40000
 |  | -00.001820000000 | 3.40000
 |  | -00.001800000000 | 3.40000
 |  | -00.001780000000 | 3.40000
 |  | -00.001760000000 | 3.40000
 |  | -00.001740000000 | 3.40000
 |  | -00.001720000000 | 3.60000
 |  | -00.001700000000 | 3.40000
 |  | -00.001680000000 | 3.60000
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

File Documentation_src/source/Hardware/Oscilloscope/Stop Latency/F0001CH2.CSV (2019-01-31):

Record Length | 2.500000e+03 | -0.002200000000 | 1.46000
Sample Interval | 2.000000e-05 | -0.002180000000 | 1.50000
Trigger Point | 1.100000000000e+02 | -0.002160000000 | 1.50000
 |  | -0.002140000000 | 1.48000
 |  | -0.002120000000 | 1.50000
 |  | -0.002100000000 | 1.48000
Source | CH2 | -0.002080000000 | 1.50000
Vertical Units | V | -0.002060000000 | 1.48000
Vertical Scale | 5.000000e-01 | -0.002040000000 | 1.46000
Vertical Offset | -9.800000e-01 | -0.002020000000 | 1.50000
Horizontal Units | s | -0.002000000000 | 1.46000
Horizontal Scale | 5.000000e-03 | -0.001980000000 | 1.48000
Pt Fmt | Y | -0.001960000000 | 1.48000
Yzero | 0.000000e+00 | -0.001940000000 | 1.48000
Probe Atten | 1.000000e+00 | -0.001920000000 | 1.48000
Model Number | TDS2012B | -0.001900000000 | 1.46000
Serial Number | C062163 | -0.001880000000 | 1.50000
Firmware Version | FV:v22.16 | -0.001860000000 | 1.48000
 |  | -00.001840000000 | 1.50000
 |  | -00.001820000000 | 1.48000
 |  | -00.001800000000 | 1.46000
 |  | -00.001780000000 | 1.50000
 |  | -00.001760000000 | 1.46000
 |  | -00.001740000000 | 1.50000
 |  | -00.001720000000 | 1.48000
 |  | -00.001700000000 | 1.46000
 |  | -00.001680000000 | 1.48000
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

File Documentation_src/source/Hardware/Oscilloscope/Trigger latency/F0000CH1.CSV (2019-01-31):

Record Length | 2.500000e+03 | -0.002200000000 | 3.40000
Sample Interval | 2.000000e-05 | -0.002180000000 | 3.40000
Trigger Point | 1.100000000000e+02 | -0.002160000000 | 3.40000
 |  | -0.002140000000 | 3.60000
 |  | -0.002120000000 | 3.40000
 |  | -0.002100000000 | 3.60000
Source | CH1 | -0.002080000000 | 3.40000
Vertical Units | V | -0.002060000000 | 3.60000
Vertical Scale | 5.000000e+00 | -0.002040000000 | 3.60000
Vertical Offset | -1.780000e+01 | -0.002020000000 | 3.40000
Horizontal Units | s | -0.002000000000 | 3.40000
Horizontal Scale | 5.000000e-03 | -0.001980000000 | 3.40000
Pt Fmt | Y | -0.001960000000 | 3.40000
Yzero | 0.000000e+00 | -0.001940000000 | 3.60000
Probe Atten | 1.000000e+00 | -0.001920000000 | 3.40000
Model Number | TDS2012B | -0.001900000000 | 3.40000
Serial Number | C062163 | -0.001880000000 | 3.60000
Firmware Version | FV:v22.16 | -0.001860000000 | 3.40000
 |  | -00.001840000000 | 3.40000
 |  | -00.001820000000 | 3.40000
 |  | -00.001800000000 | 3.40000
 |  | -00.001780000000 | 3.40000
 |  | -00.001760000000 | 3.40000
 |  | -00.001740000000 | 3.40000
 |  | -00.001720000000 | 3.40000
 |  | -00.001700000000 | 3.40000
 |  | -00.001680000000 | 3.40000
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

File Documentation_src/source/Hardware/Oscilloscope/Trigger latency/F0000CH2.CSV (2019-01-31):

Record Length | 2.500000e+03 | -0.002200000000 | 0.06000
Sample Interval | 2.000000e-05 | -0.002180000000 | 0.06000
Trigger Point | 1.100000000000e+02 | -0.002160000000 | 0.06000
 |  | -0.002140000000 | 0.04000
 |  | -0.002120000000 | 0.04000
 |  | -0.002100000000 | 0.06000
Source | CH2 | -0.002080000000 | 0.02000
Vertical Units | V | -0.002060000000 | 0.04000
Vertical Scale | 5.000000e-01 | -0.002040000000 | 0.04000
Vertical Offset | -9.800000e-01 | -0.002020000000 | 0.04000
Horizontal Units | s | -0.002000000000 | 0.06000
Horizontal Scale | 5.000000e-03 | -0.001980000000 | 0.06000
Pt Fmt | Y | -0.001960000000 | 0.04000
Yzero | 0.000000e+00 | -0.001940000000 | 0.06000
Probe Atten | 1.000000e+00 | -0.001920000000 | 0.04000
Model Number | TDS2012B | -0.001900000000 | 0.04000
Serial Number | C062163 | -0.001880000000 | 0.06000
Firmware Version | FV:v22.16 | -0.001860000000 | 0.04000
 |  | -00.001840000000 | 0.04000
 |  | -00.001820000000 | 0.06000
 |  | -00.001800000000 | 0.04000
 |  | -00.001780000000 | 0.04000
 |  | -00.001760000000 | 0.06000
 |  | -00.001740000000 | 0.06000
 |  | -00.001720000000 | 0.04000
 |  | -00.001700000000 | 0.04000
 |  | -00.001680000000 | 0.04000
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

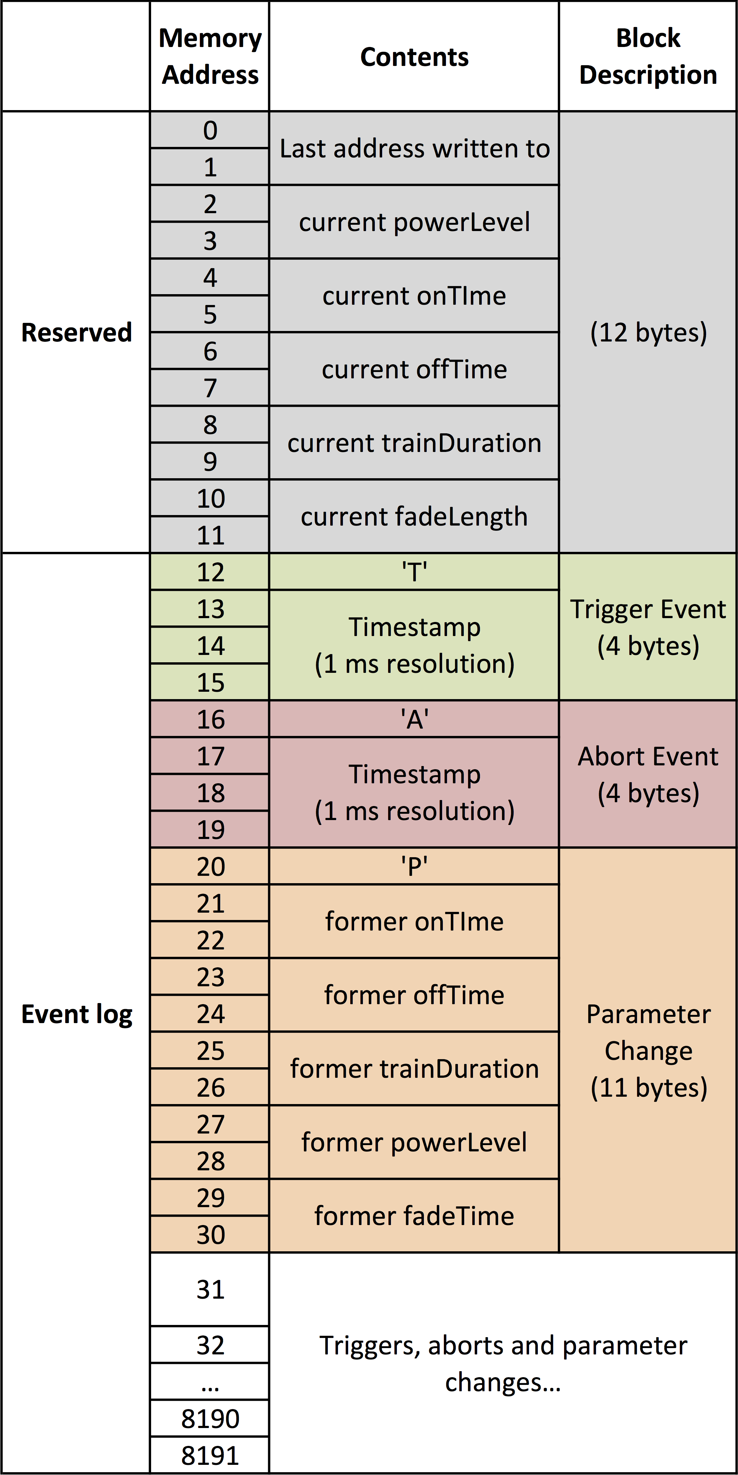
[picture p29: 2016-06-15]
Documentation_src/source/Hardware/photos/memory layout.png

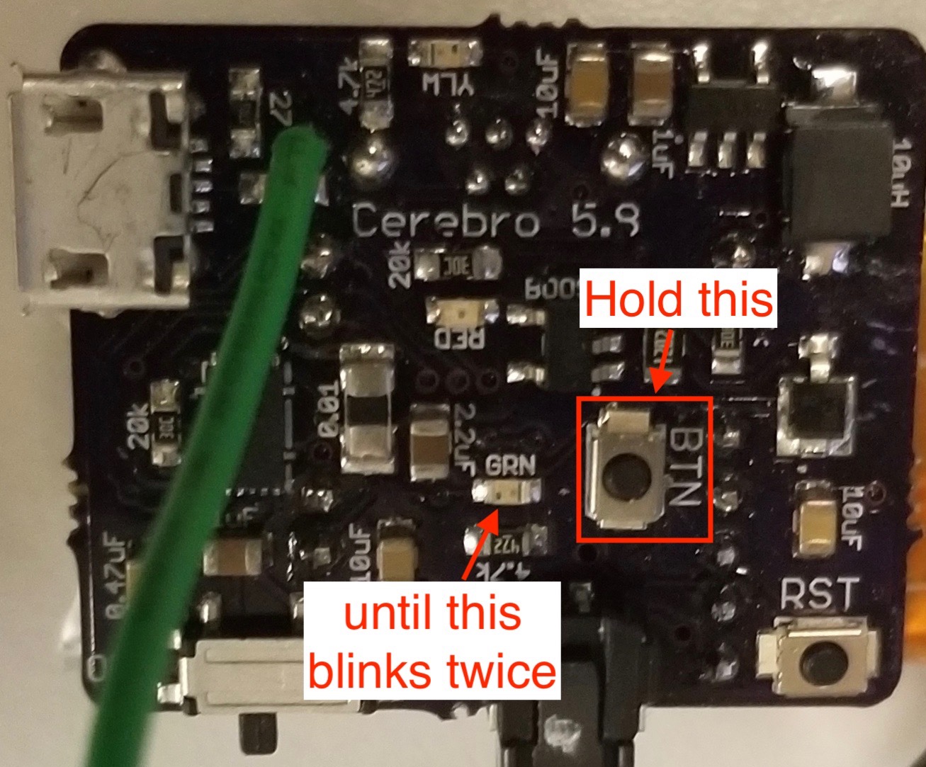
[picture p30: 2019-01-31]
Documentation_src/source/Hardware/photos/serial_number/hold.jpg

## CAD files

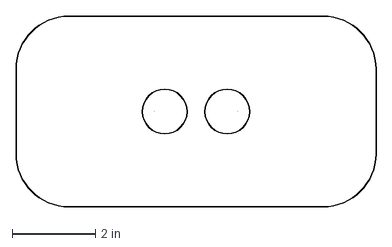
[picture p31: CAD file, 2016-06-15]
docs/_downloads/30b0d53e4af14b1d5fc3d113b661c4af/Fiber guide_1,5mm gap.dxf
8.63 x 4.57 in

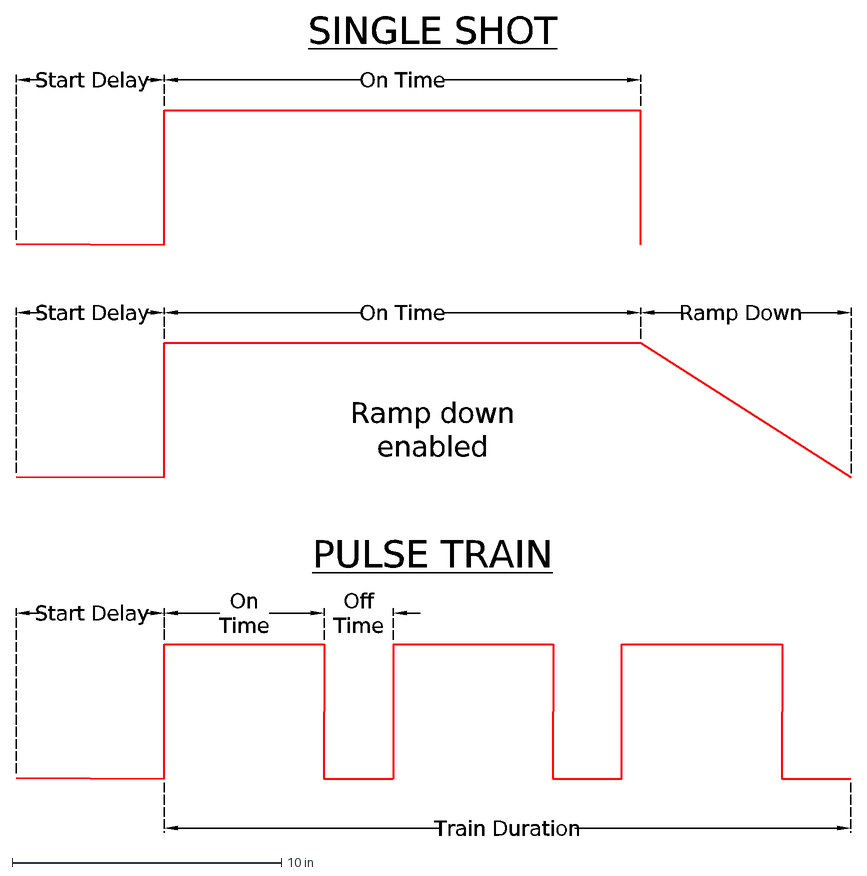
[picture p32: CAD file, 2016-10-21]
Docs/source/Software/photos/Edit_waveform/Or/pulse parameters.dxf
Train Duration
On Time
SINGLE SHOT
PULSE TRAIN
Off Time
Ramp Down
Ramp down enabled
Start Delay

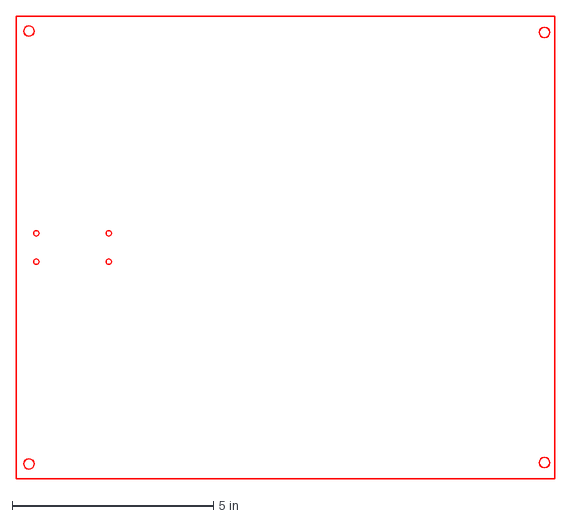
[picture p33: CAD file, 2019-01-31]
Lasercut/Behavior box top/Behavior box top.dxf
13.4 x 11.5 in

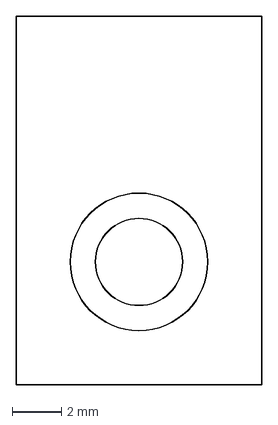
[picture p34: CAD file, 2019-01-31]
Lasercut/fiber alignment jig.dxf
10.0 x 15.0 mm

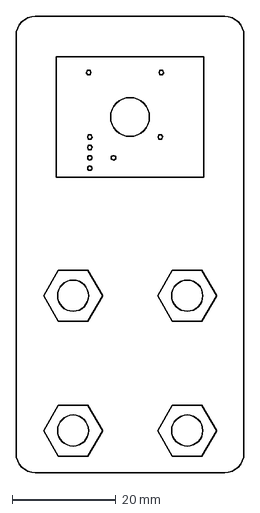
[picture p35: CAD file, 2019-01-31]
Lasercut/Programming jig/jig.dxf
43.9 x 88.0 mm

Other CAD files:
Lasercut/3axis plate.dxf

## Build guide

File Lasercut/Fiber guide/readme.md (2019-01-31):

## ID&F Laser Settings
- Continuous Cast Acrylic
- 0.125" thickness
- Vector Performance: all the way left = Quality
- Vector Cutting: -30%
- Top and bottom Lasers both on
- High density (HD) head

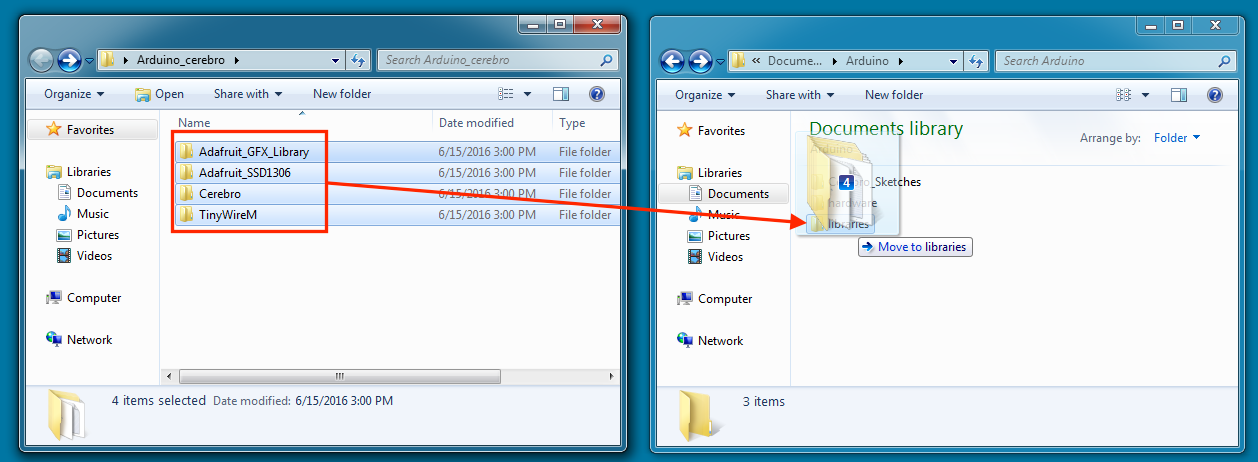
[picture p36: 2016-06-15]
Documentation_src/source/Hardware/photos/Arduino_Setup/transfer_libraries.png

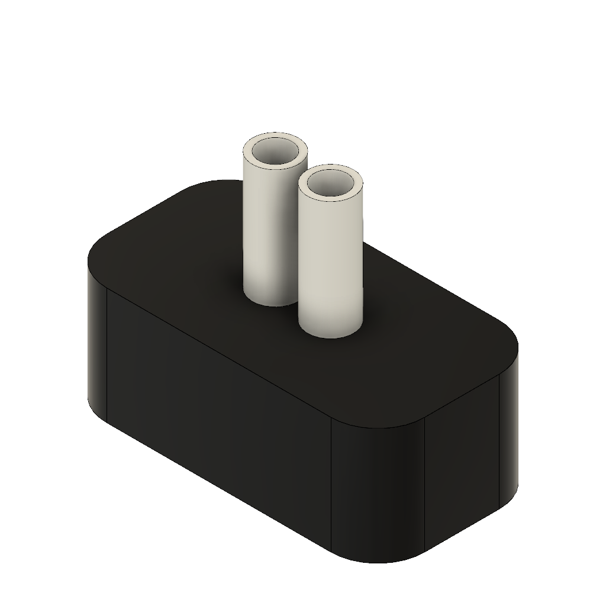
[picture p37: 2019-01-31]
Documentation_src/source/Hardware/photos/Implant_construction/make_guide/fiber guide v3_top.png

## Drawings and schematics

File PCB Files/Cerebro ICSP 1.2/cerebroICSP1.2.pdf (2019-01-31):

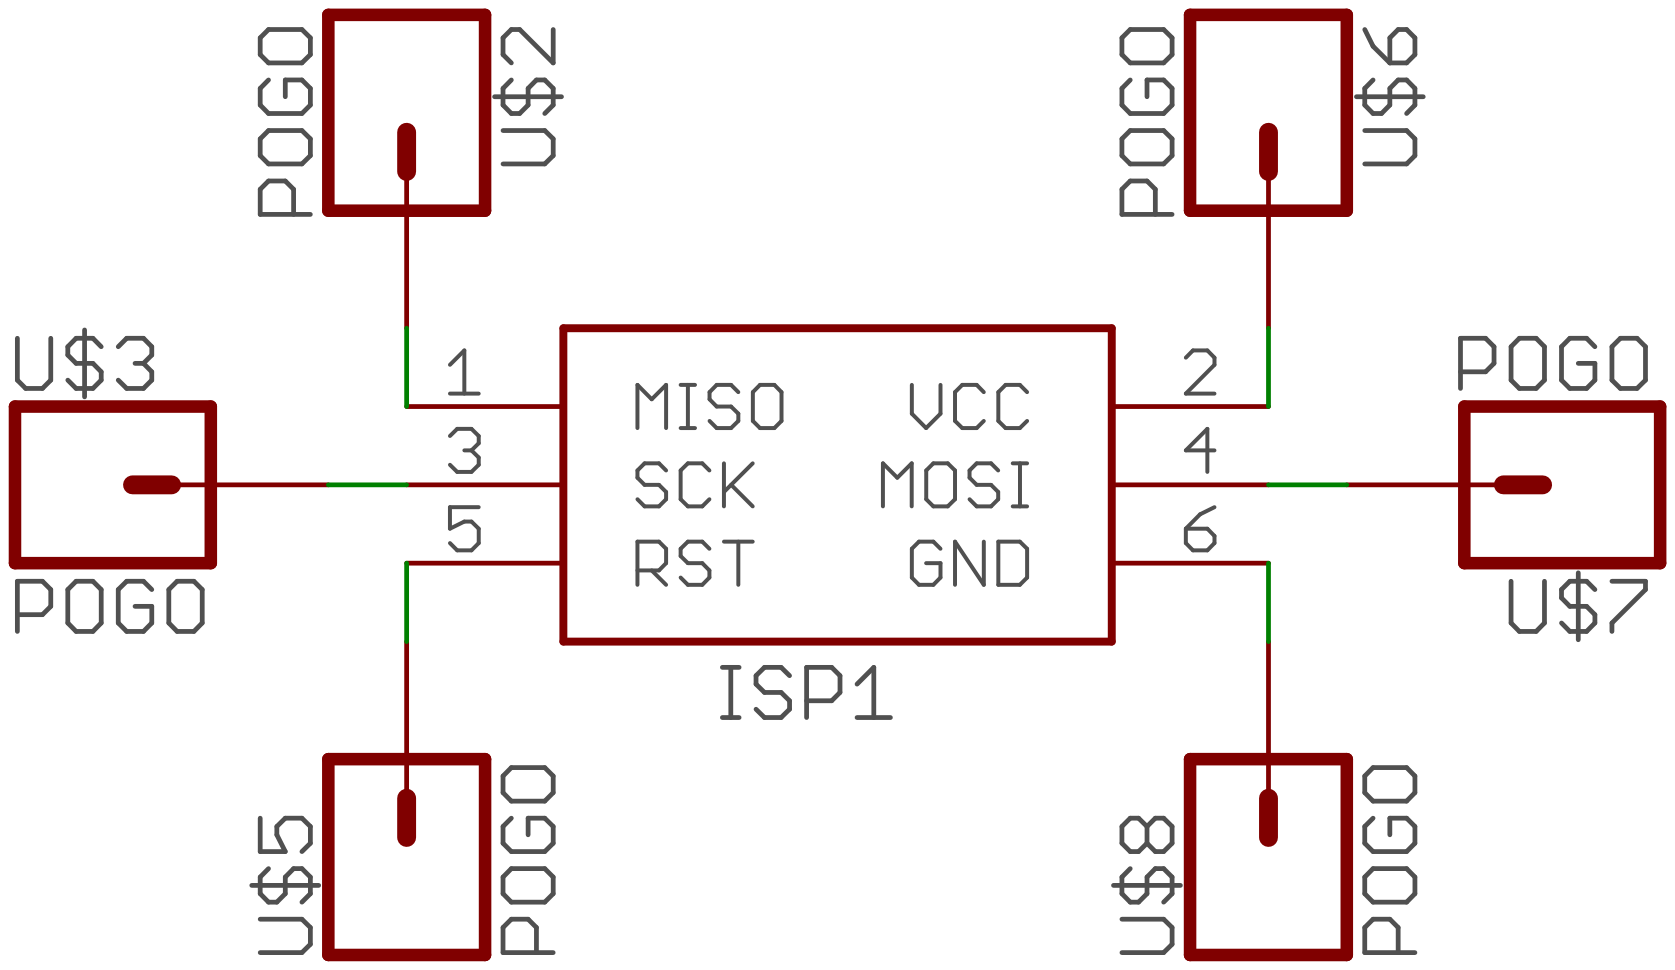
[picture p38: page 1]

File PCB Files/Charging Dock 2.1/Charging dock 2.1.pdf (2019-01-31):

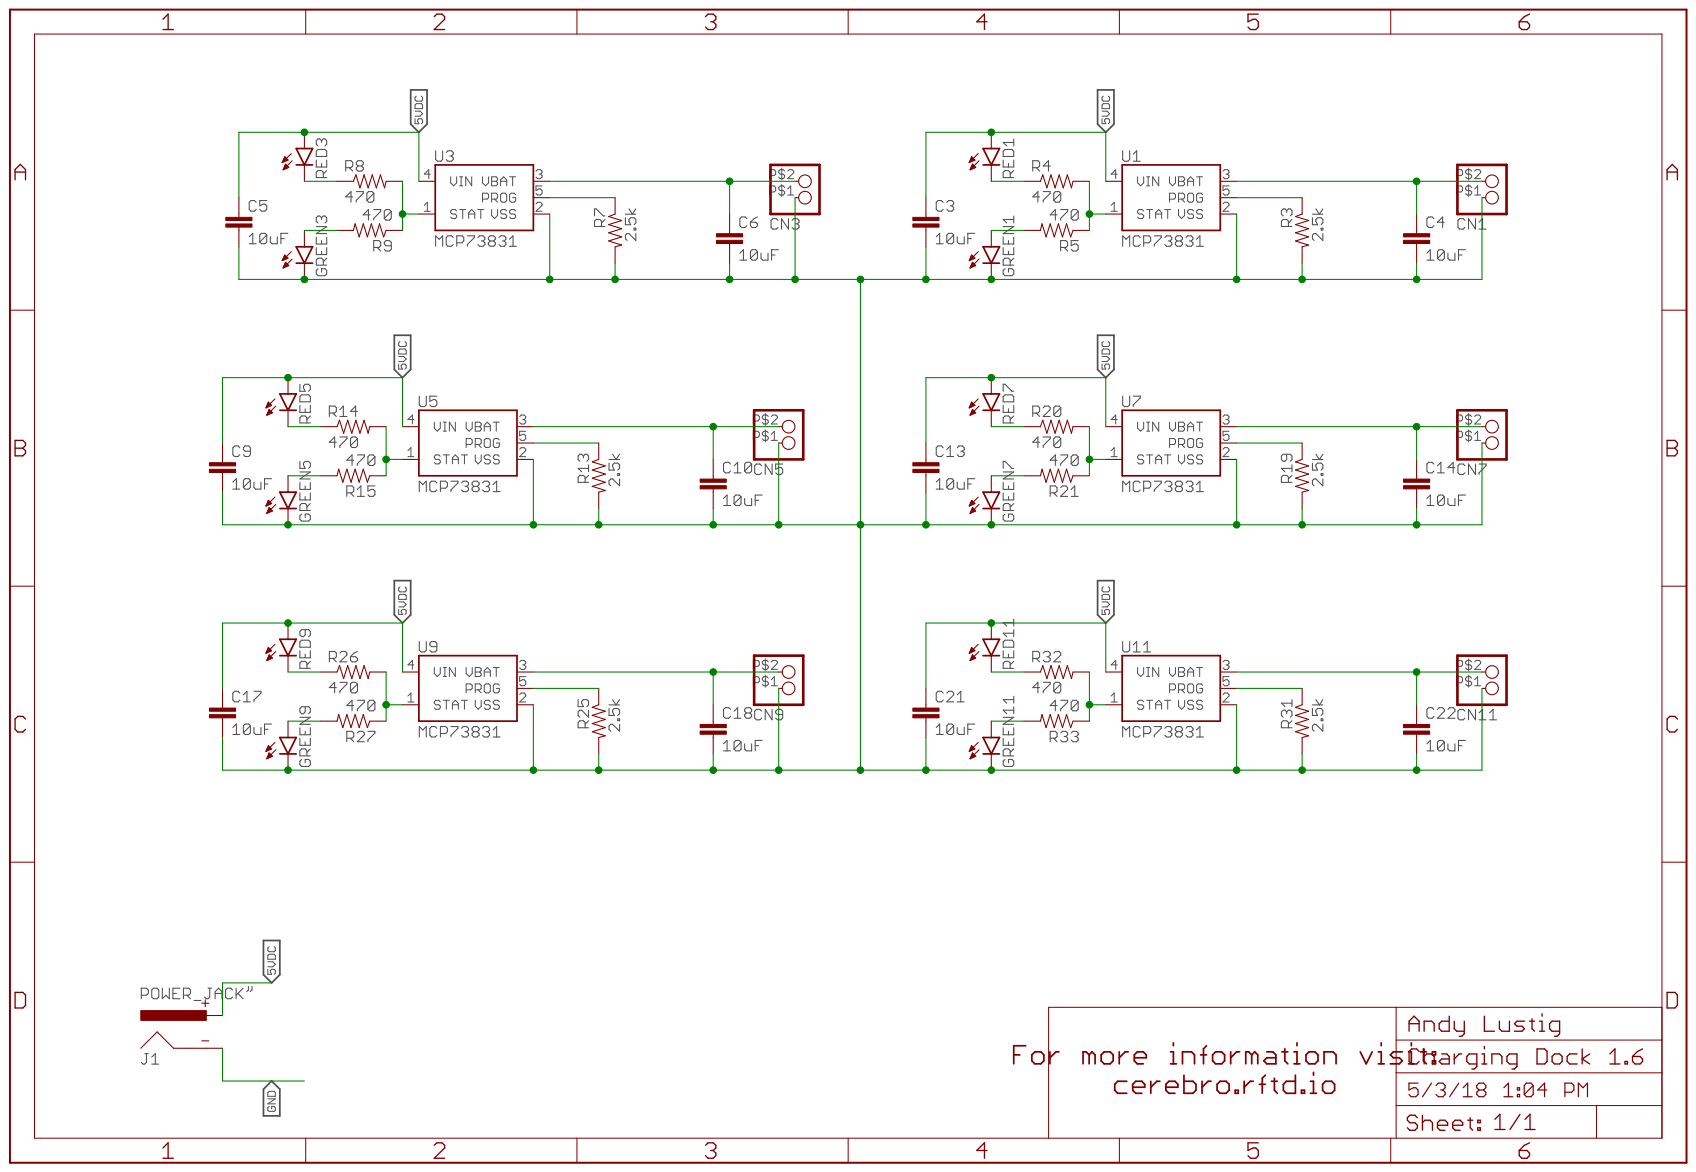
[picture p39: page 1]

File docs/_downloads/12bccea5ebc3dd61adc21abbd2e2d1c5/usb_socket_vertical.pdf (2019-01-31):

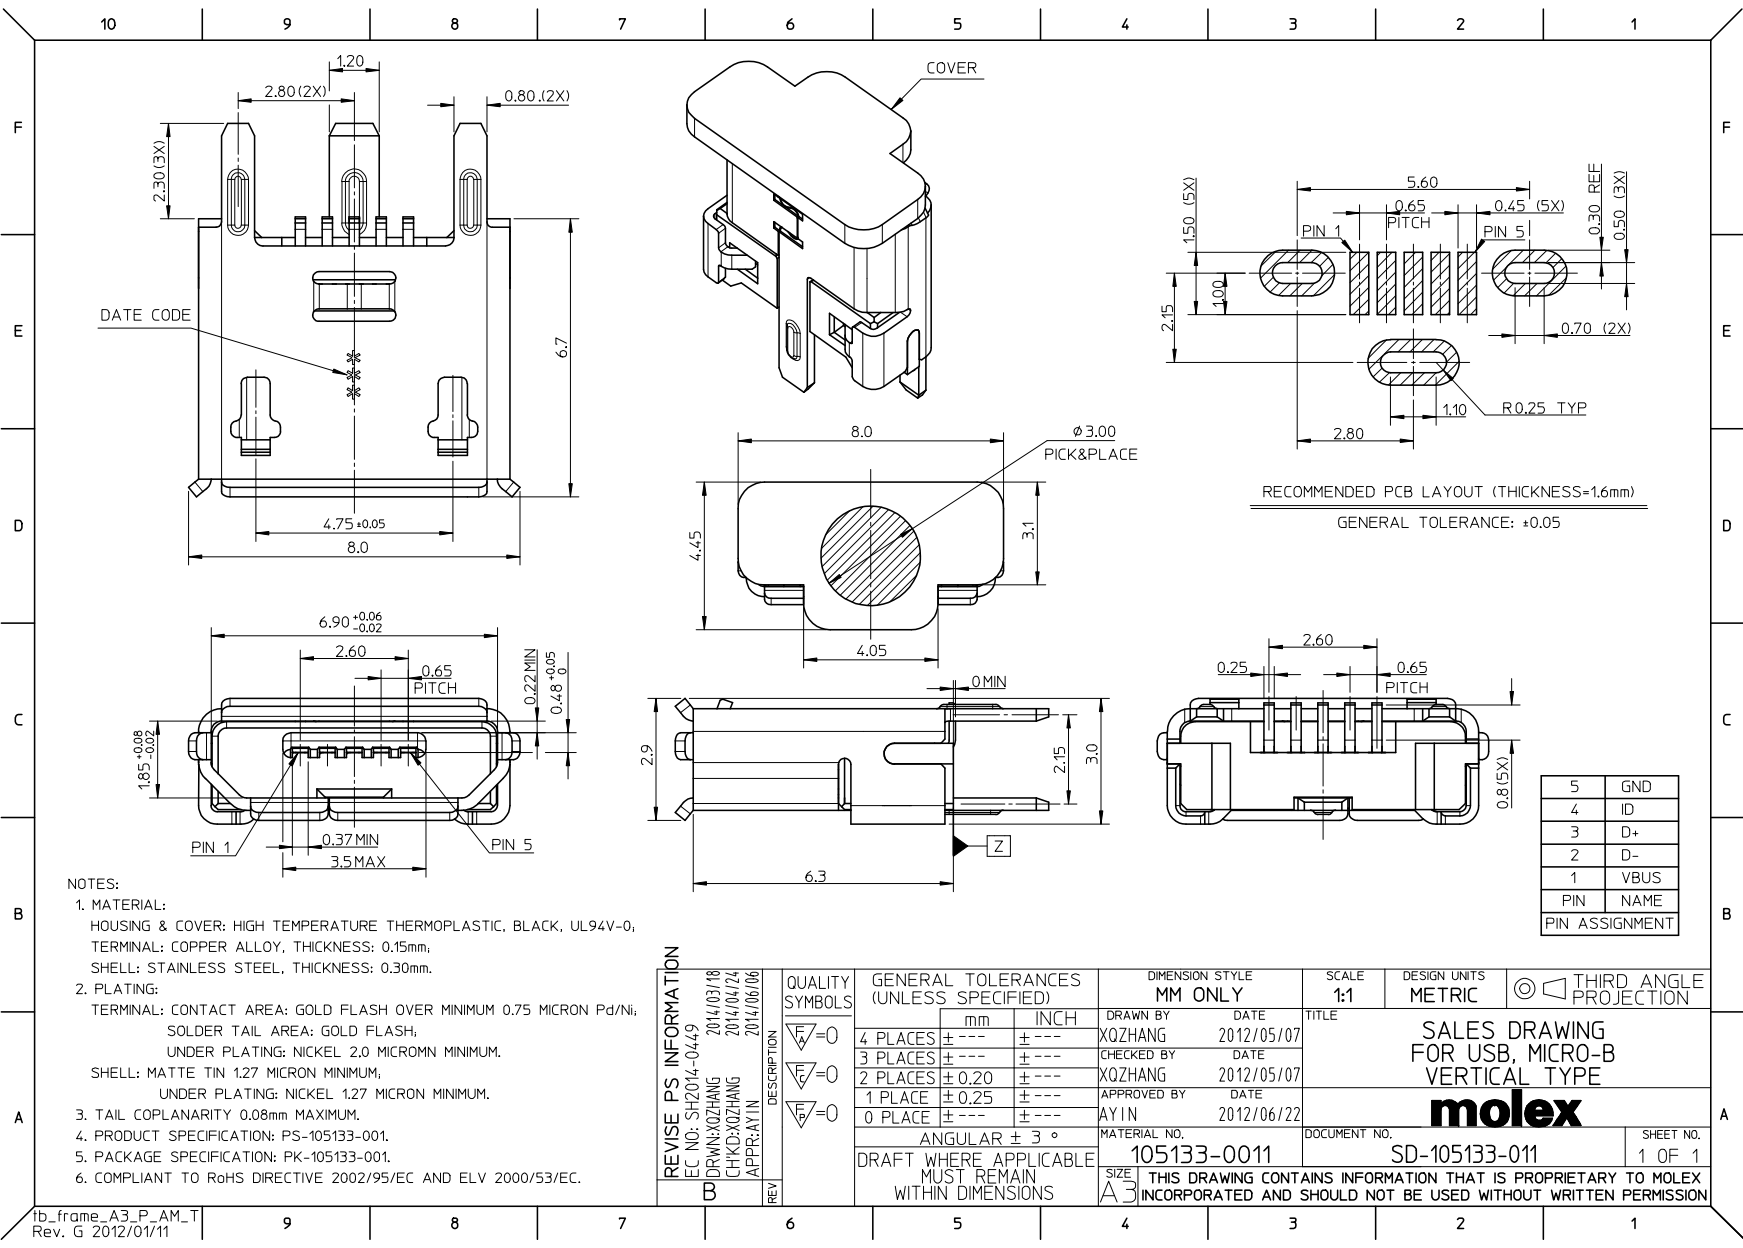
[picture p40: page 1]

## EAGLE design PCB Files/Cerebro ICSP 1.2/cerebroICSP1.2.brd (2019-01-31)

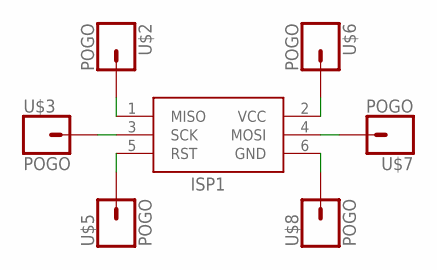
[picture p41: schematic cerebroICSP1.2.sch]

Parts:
ISP1: AVRISP-BOX
U$2, U$3, U$5, U$6, U$7, U$8: POGO

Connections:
unnamed: ISP1.1 (MISO), U$2.P$1
unnamed: ISP1.3 (SCK), U$3.P$1
unnamed: ISP1.5 (RST), U$5.P$1
unnamed: ISP1.2 (VCC), U$6.P$1
unnamed: ISP1.4 (MOSI), U$7.P$1
unnamed: ISP1.6 (GND), U$8.P$1

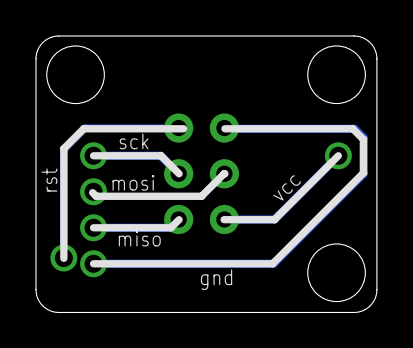
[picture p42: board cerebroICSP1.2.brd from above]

Board: 2 copper layers, 18.9 x 15.4 mm, 7 parts (1 on the bottom side), 6 nets.

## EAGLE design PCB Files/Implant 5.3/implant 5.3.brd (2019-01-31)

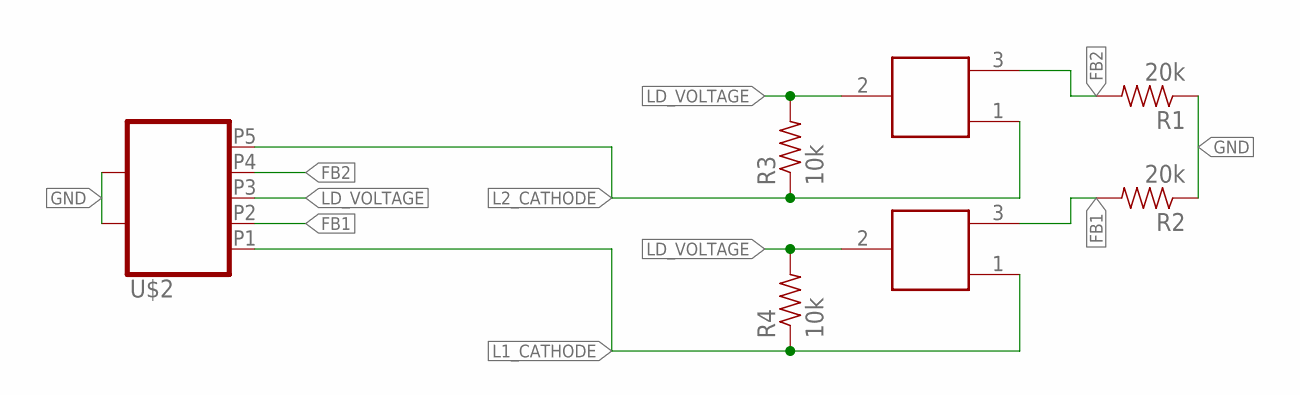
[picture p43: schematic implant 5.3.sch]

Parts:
R1, R2: 20k; 0805
R3, R4: 10k; 0805
U$2: USB_MICRO_SOCKET_VERT; USB_VERT_MICRO_SMD
U$6, U$7: LASERDIODE5.6MM; LASERDIODE_5.6

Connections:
FB1: R2.2, U$2.P2, U$6.3
FB2: R1.2, U$2.P4, U$7.3
GND: R1.1, R2.1, U$2.P$1, U$2.P$2, U$2.P$3
L1_CATHODE: R4.1, U$2.P1, U$6.1
L2_CATHODE: R3.1, U$2.P5, U$7.1
LD_VOLTAGE: R3.2, R4.2, U$2.P3, U$6.2, U$7.2

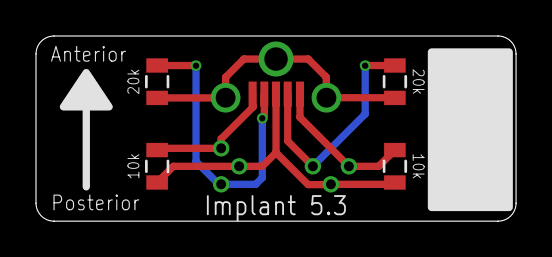
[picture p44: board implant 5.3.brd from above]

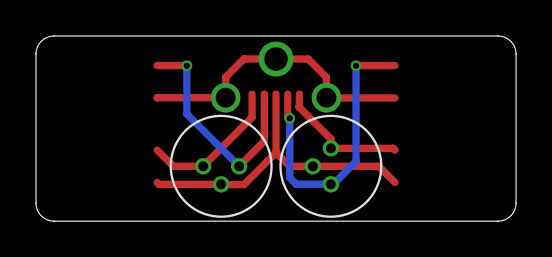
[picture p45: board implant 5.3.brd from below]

Board: 2 copper layers, 26.7 x 10.3 mm, 7 parts (2 on the bottom side), 6 nets.

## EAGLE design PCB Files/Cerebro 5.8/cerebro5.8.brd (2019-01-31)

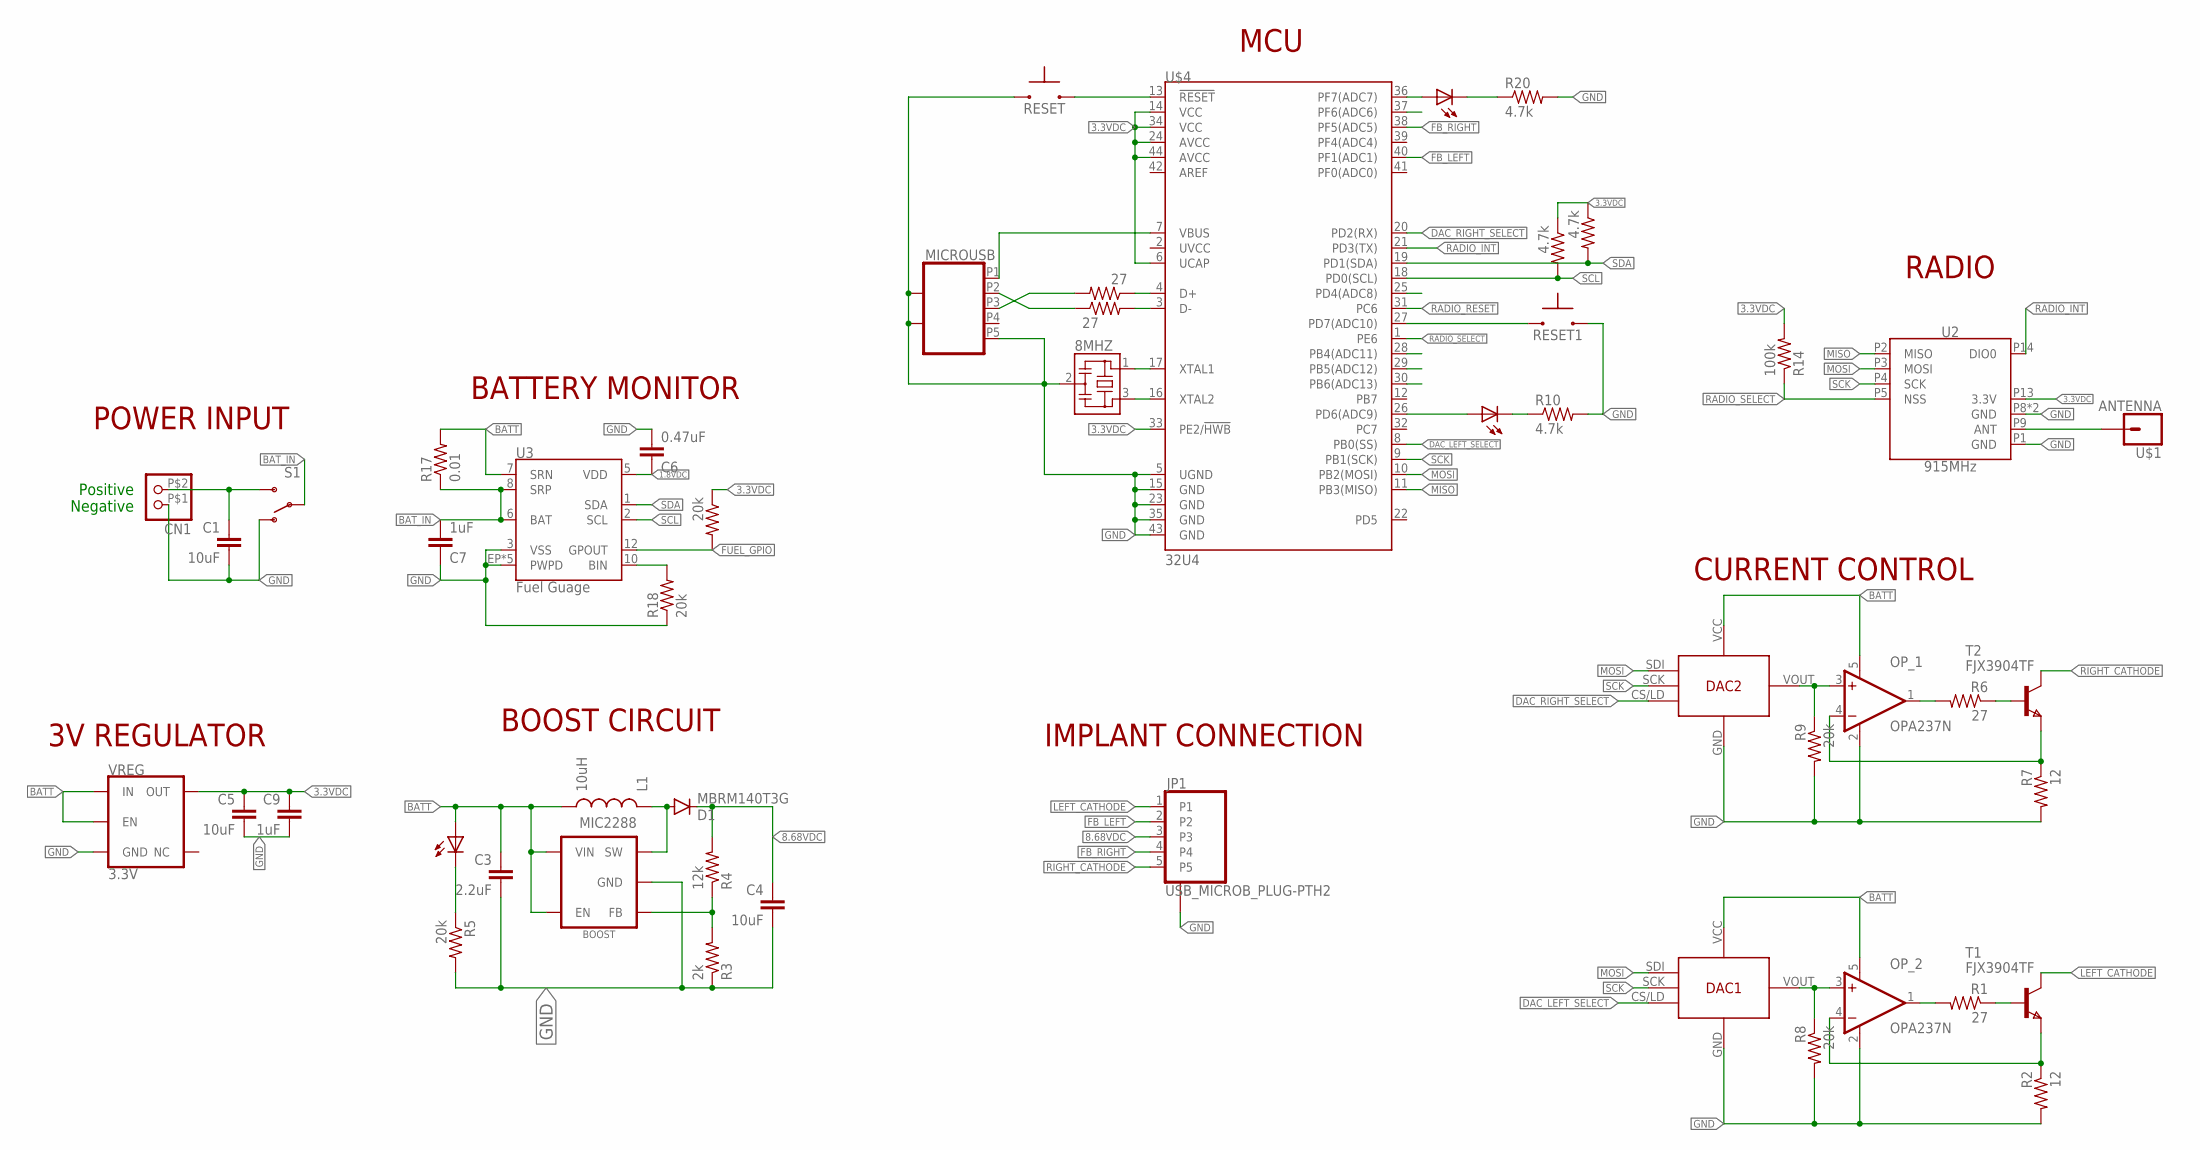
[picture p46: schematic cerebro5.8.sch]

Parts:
8MHZ: RESONATOR_CSTCE_V; CSTCE_V
C1, C4, C5: 10uF; 0805
C3: 2.2uF; 0805
C6: 0.47uF; 0805
C7, C9: 1uF; 0805
CN1: JST_2PINMICRO; MICRO_LOCK_2PIN
D1: MBRM140T3G; POWERMITE
DAC1, DAC2: DAC; SC-70
INDICATOR_LED: RED; CHIP-LED0603
INDICATOR_LED1: YLW; CHIP-LED0603
INDICATOR_LED2: GRN; CHIP-LED0603
JP1: USB_MICROB_PLUG-PTH2; MICRO-B-TH
L1: 10uH; 1812
MIC2288: BOOST; SOT23-5
MICROUSB: USB_MICRO_SOCKET_HORZ_REINFORCED; USB_HORZ_REINFORCED_MICRO
OP_1, OP_2: OPA237N; SOT23-5
R1, R6, R12, R13: 27; 0603-RES
R2, R7: 12; 0603-RES
R3: 2k; 0603-RES
R4: 12k; 0805
R5, R8, R9, R18, R19: 20k; 0603-RES
R10, R15, R16, R20: 4.7k; 0603-RES
R14: 100k; 0603-RES
R17: 0.01; 1206
RESET, RESET1: SWITCH-MOMENTARY-NO; SWITCH_MOMENTARY_XS
S1: SWITCH-SPDTREINFORCED_SMD; SWITCH-SPDT-SMD-REINFORCED
T1, T2: FJX3904TF; SOT323
U2: 915MHz; RFM69HCW-XXXS2
U3: Fuel Guage; PDSO-N12
U$1: ANTENNA; 1X01
U$4: 32U4; QFN-44-NOPAD
VREG: 3.3V; SOT23-5

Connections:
1.8VDC: C6.1, U3.5 (VDD)
3.3VDC: C5.1, C9.1, R14.2, R15.1, R16.1, R19.1, U2.P13 (3.3V), U$4.6 (UCAP), U$4.14 (VCC), U$4.24 (AVCC), U$4.33 (PE2/!HWB), U$4.34 (VCC), U$4.44 (AVCC), VREG.5 (OUT)
8.68VDC: C4.1, D1.CATHODE (C), JP1.3, R4.2
BATT: C3.1, DAC1.VCC (VIN), DAC2.VCC (VIN), INDICATOR_LED.A, L1.P$2 (2), L1.P$4 (2), MIC2288.4 (EN), MIC2288.5 (VIN), OP_1.5 (V+), OP_2.5 (V+), R17.2, U3.7 (SRN), VREG.1 (IN), VREG.3 (EN)
BAT_IN: C7.2, R17.1, S1.2, U3.6 (BAT), U3.8 (SRP)
DAC_LEFT_SELECT: DAC1.CS/LD, U$4.8 (PB0(SS))
DAC_RIGHT_SELECT: DAC2.CS/LD, U$4.20 (PD2(RX))
FB_LEFT: JP1.2, U$4.40 (PF1(ADC1))
FB_RIGHT: JP1.4, U$4.38 (PF5(ADC5))
FUEL_GPIO: R19.2, U3.12 (GPOUT)
GND: 8MHZ.2, C1.2, C3.2, C4.2, C5.2, C6.2, C7.1, C9.2, CN1.P$1 (1), DAC1.GND, DAC2.GND, JP1.P$1 (GND_PINS), JP1.P$2 (GND_PINS), MIC2288.2 (GND), MICROUSB.G1, MICROUSB.G2, MICROUSB.P5, MICROUSB.P$1, MICROUSB.P$2, OP_1.2 (V-), OP_2.2 (V-), R2.2, R3.1, R5.2, R7.2, R8.2, R9.2, R10.2, R18.1, R20.2, RESET.P$1 (1), RESET1.P$2 (2), S1.1 (O), U2.P1 (GND), U2.P8 (GND), U2.P10 (GND), U3.3 (VSS), U3.EP (PWPD), U3.EP1 (PWPD), U3.EP2 (PWPD), U3.EP3 (PWPD), U3.EP4 (PWPD), U$4.5 (UGND), U$4.15 (GND), U$4.23 (GND), U$4.35 (GND), U$4.43 (GND), VREG.2 (GND)
LEFT_CATHODE: JP1.1, T1.1 (C)
MISO: U2.P2 (MISO), U$4.11 (PB3(MISO))
MOSI: DAC1.SDI, DAC2.SDI, U2.P3 (MOSI), U$4.10 (PB2(MOSI))
unnamed: DAC2.VOUT, OP_1.3 (+IN), R9.1
unnamed: OP_1.4 (-IN), R7.1, T2.3 (E)
unnamed: DAC1.VOUT, OP_2.3 (+IN), R8.1
unnamed: C1.1, CN1.P$2 (2), S1.3 (S)
unnamed: OP_1.1 (OUT), R6.2
unnamed: OP_2.4 (-IN), R2.1, T1.3 (E)
unnamed: R6.1, T2.2 (B)
unnamed: INDICATOR_LED.C, R5.1
unnamed: OP_2.1 (OUT), R1.2
unnamed: MIC2288.3 (FB), R3.2, R4.1
unnamed: R1.1, T1.2 (B)
unnamed: 8MHZ.1, U$4.17 (XTAL1)
unnamed: 8MHZ.3, U$4.16 (XTAL2)
unnamed: MICROUSB.P1, U$4.7 (VBUS)
unnamed: D1.ANODE (A), L1.P$1 (1), L1.P$3 (1), MIC2288.1 (SW)
unnamed: R12.1, U$4.4 (D+)
unnamed: R13.2, U$4.3 (D-)
unnamed: MICROUSB.P3, R12.2
unnamed: MICROUSB.P2, R13.1
unnamed: INDICATOR_LED2.C, R10.1
unnamed: RESET1.P$1 (1), U$4.27 (PD7(ADC10))
unnamed: U2.P9 (ANT), U$1.1
unnamed: INDICATOR_LED1.C, R20.1
unnamed: INDICATOR_LED1.A, U$4.36 (PF7(ADC7))
unnamed: R18.2, U3.10 (BIN)
unnamed: INDICATOR_LED2.A, U$4.26 (PD6(ADC9))
RADIO_INT: U2.P14 (DIO0), U$4.21 (PD3(TX))
RADIO_RESET: U$4.31 (PC6)
RADIO_SELECT: R14.1, U2.P5 (NSS), U$4.1 (PE6)
RESET: RESET.P$2 (2), U$4.13 (!RESET)
RIGHT_CATHODE: JP1.5, T2.1 (C)
SCK: DAC1.SCK, DAC2.SCK, U2.P4 (SCK), U$4.9 (PB1(SCK))
SCL: R15.2, U3.2 (SCL), U$4.18 (PD0(SCL))
SDA: R16.2, U3.1 (SDA), U$4.19 (PD1(SDA))

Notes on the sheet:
Positive
Negative
BOOST CIRCUIT
CURRENT CONTROL
RADIO
3V REGULATOR
BATTERY MONITOR
POWER INPUT
IMPLANT CONNECTION
MCU

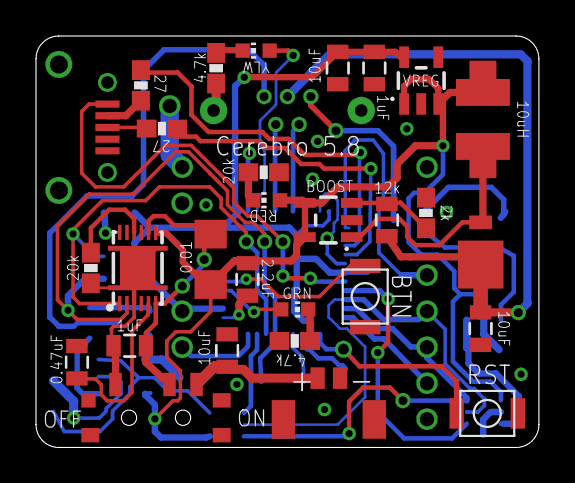
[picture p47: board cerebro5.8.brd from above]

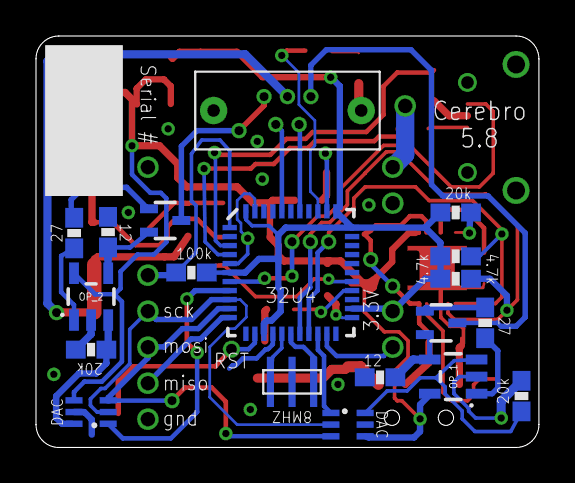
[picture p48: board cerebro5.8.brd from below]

Board: 2 copper layers, 27.9 x 22.9 mm, 50 parts (19 on the bottom side), 47 nets.

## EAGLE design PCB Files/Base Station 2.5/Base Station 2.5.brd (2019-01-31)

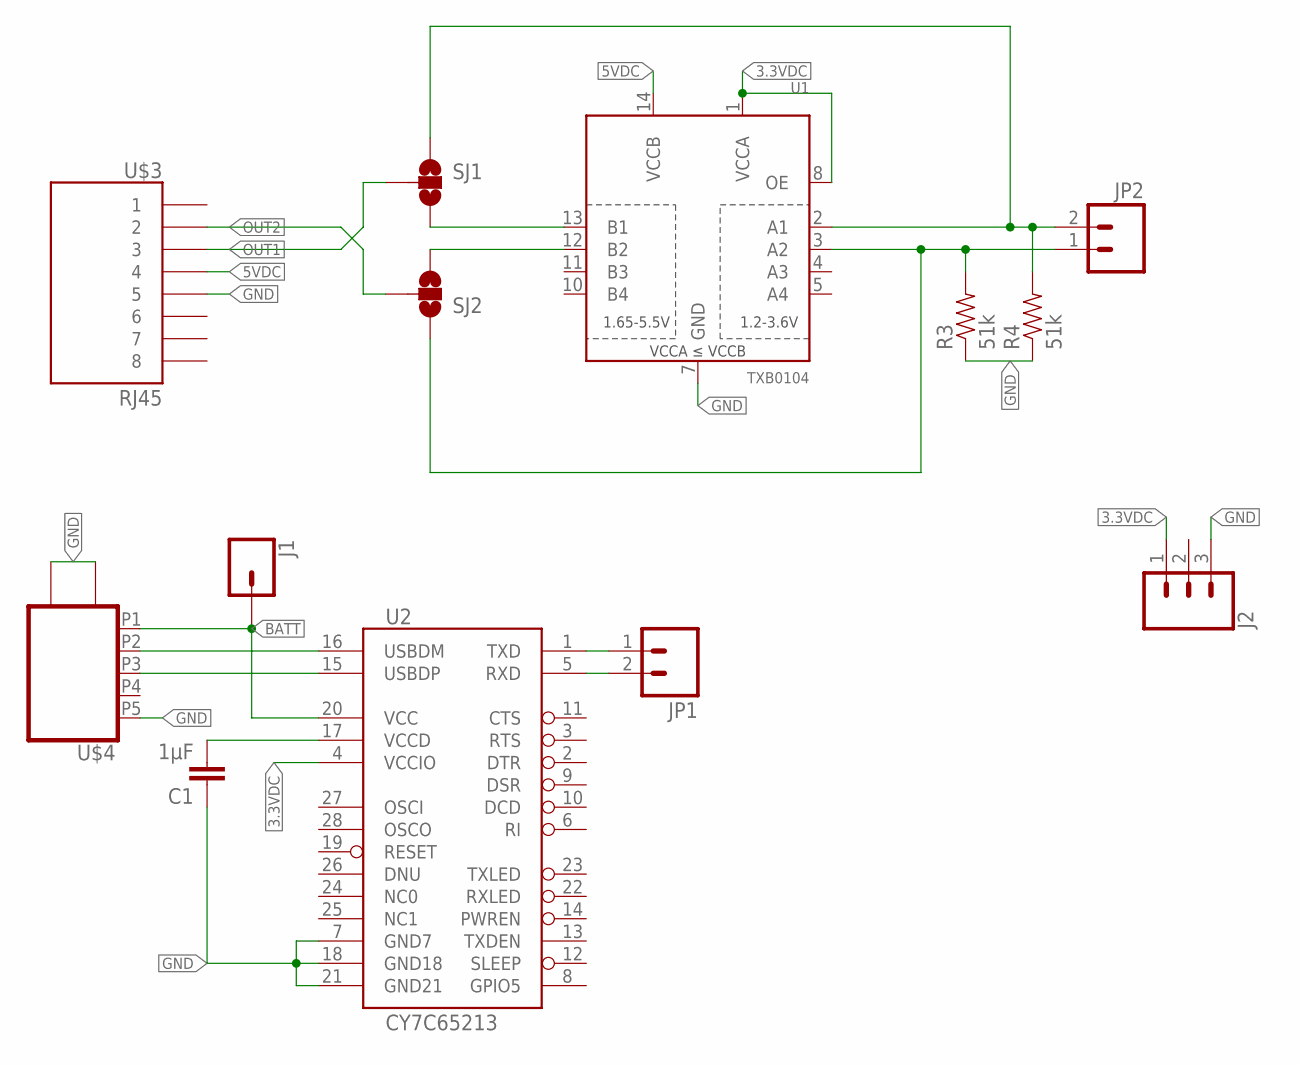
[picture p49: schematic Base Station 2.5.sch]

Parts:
C1: 1µF; 0603
J1: CONN_01PTH_NO_SILK_YES_STOP; 1X01_NO_SILK
J2: CONN_031X03_NO_SILK; 1X03_NO_SILK
JP1, JP2: M021X02_NO_SILK; 1X02_NO_SILK
R3, R4: 51k; 0805
SJ1, SJ2: SOLDERJUMPER_2WAYPASTE2&3; SJ_3_PASTE2&3
U1: TXB0104; TSSOP14
U2: CY7C65213; SSOP28DB
U$3: RJ45; RJ45-8
U$4: USB_MICRO_SOCKET_HORZ_REINFORCED; USB_HORZ_REINFORCED_MICRO

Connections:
3.3VDC: J2.1, U1.1 (VCCA), U1.8 (OE), U2.4 (VCCIO)
5VDC: U1.14 (VCCB), U$3.4
BATT: J1.1, U2.20 (VCC), U$4.P1
GND: C1.1, J2.3, R3.1, R4.1, U1.7 (GND), U2.7 (GND7), U2.18 (GND18), U2.21 (GND21), U$3.5, U$4.G1, U$4.G2, U$4.P5, U$4.P$1, U$4.P$2
unnamed: JP1.1, U2.1 (TXD)
unnamed: JP1.2, U2.5 (RXD)
unnamed: U2.15 (USBDP), U$4.P3
unnamed: U2.16 (USBDM), U$4.P2
unnamed: C1.2, U2.17 (VCCD)
unnamed: JP2.2, R4.2, SJ1.1, U1.2 (A1)
unnamed: JP2.1, R3.2, SJ2.1, U1.3 (A2)
unnamed: SJ2.3, U1.12 (B2)
unnamed: SJ1.3, U1.13 (B1)
NC1: U2.25 (NC1)
OUT1: SJ1.2, U$3.3
OUT2: SJ2.2, U$3.2

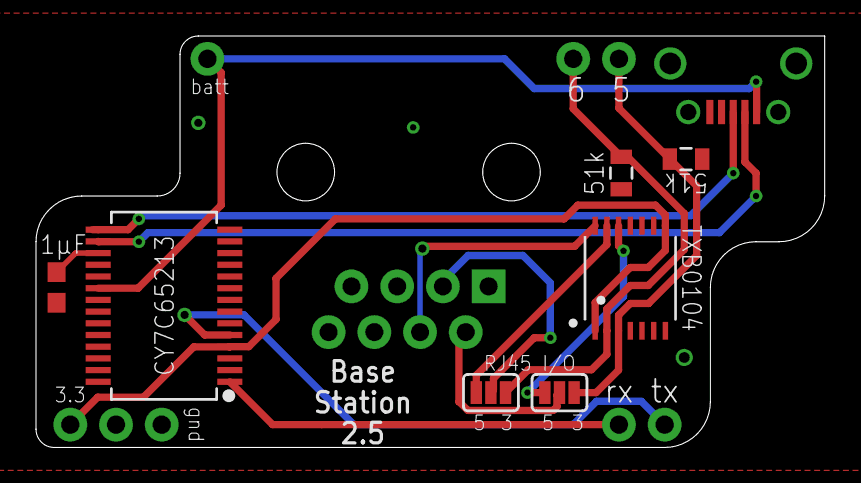
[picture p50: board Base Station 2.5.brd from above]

Board: 2 copper layers, 43.8 x 22.9 mm, 13 parts (0 on the bottom side), 15 nets.

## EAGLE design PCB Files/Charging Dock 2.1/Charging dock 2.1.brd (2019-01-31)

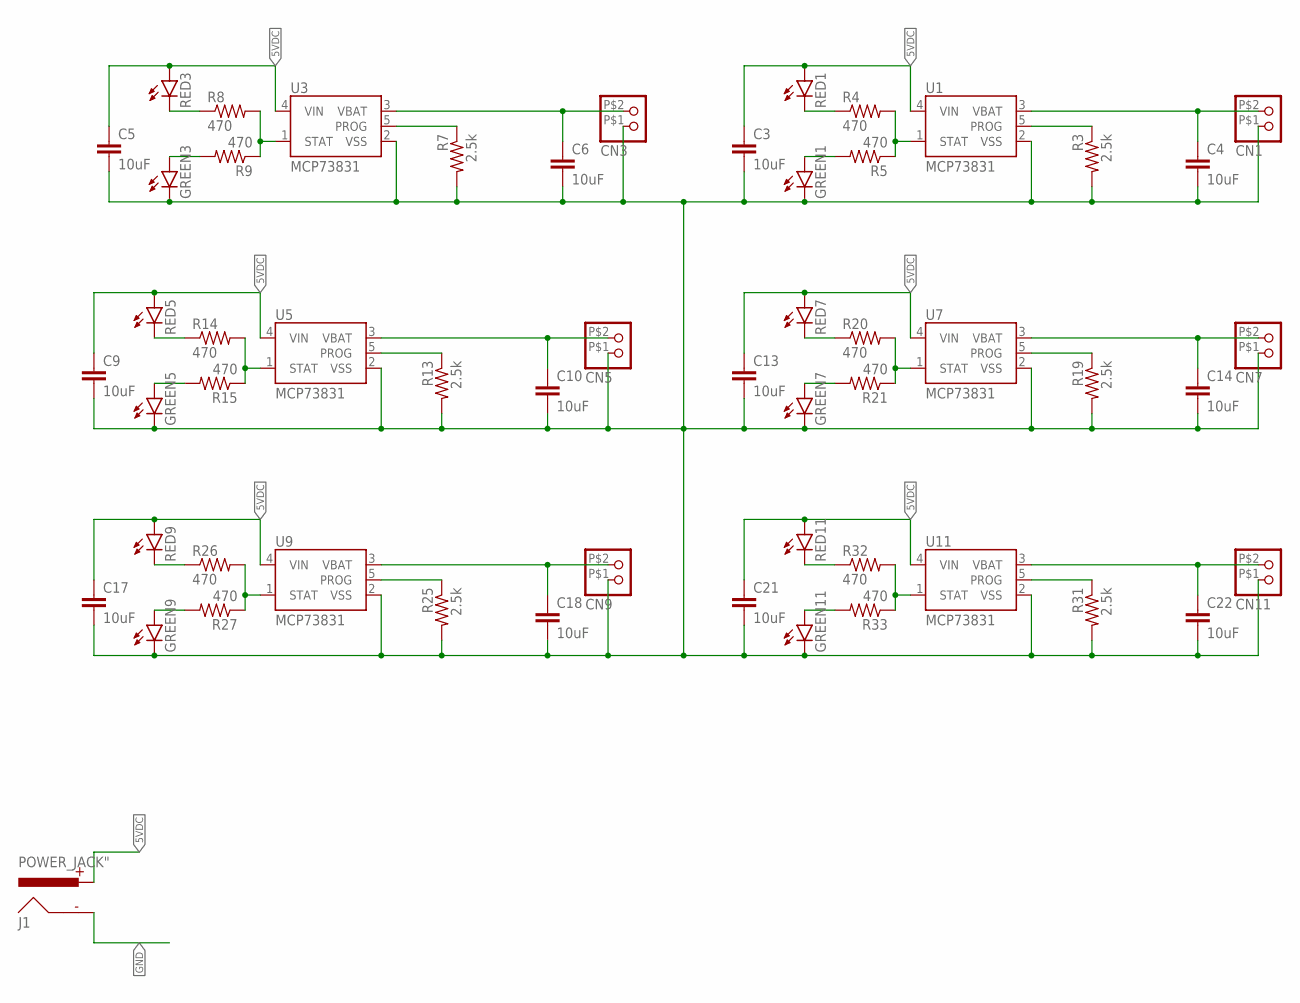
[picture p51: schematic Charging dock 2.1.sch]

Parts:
C3, C4, C5, C6, C9, C10, C13, C14, C17, C18, C21, C22: 10uF; 0805
CN1, CN3, CN5, CN7, CN9, CN11: JST_2PINMICRO; MICRO_LOCK_2PIN
GREEN1, GREEN3, GREEN5, GREEN7, GREEN9, GREEN11: LED3MM
J1: POWER_JACK"; BARREL_CONN
R3, R7, R13, R19, R25, R31: 2.5k; 0805
R4, R5, R8, R9, R14, R15, R20, R21, R26, R27, R32, R33: 470; 0805
RED1, RED3, RED5, RED7, RED9, RED11: LED3MM
U1, U3, U5, U7, U9, U11: MCP73831; SOT23-5

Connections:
5VDC: C3.1, C5.1, C9.1, C13.1, C17.1, C21.1, J1.PWR, RED1.A, RED3.A, RED5.A, RED7.A, RED9.A, RED11.A, U1.4 (VIN), U3.4 (VIN), U5.4 (VIN), U7.4 (VIN), U9.4 (VIN), U11.4 (VIN)
GND: C3.2, C4.2, C5.2, C6.2, C9.2, C10.2, C13.2, C14.2, C17.2, C18.2, C21.2, C22.2, CN1.P$1 (1), CN3.P$1 (1), CN5.P$1 (1), CN7.P$1 (1), CN9.P$1 (1), CN11.P$1 (1), GREEN1.K (C), GREEN3.K (C), GREEN5.K (C), GREEN7.K (C), GREEN9.K (C), GREEN11.K (C), J1.GND, R3.2, R7.2, R13.2, R19.2, R25.2, R31.2, U1.2 (VSS), U3.2 (VSS), U5.2 (VSS), U7.2 (VSS), U9.2 (VSS), U11.2 (VSS)
unnamed: R3.1, U1.5 (PROG)
unnamed: R4.1, RED1.K (C)
unnamed: R4.2, R5.1, U1.1 (STAT)
unnamed: GREEN1.A, R5.2
unnamed: R7.1, U3.5 (PROG)
unnamed: R8.1, RED3.K (C)
unnamed: R8.2, R9.1, U3.1 (STAT)
unnamed: GREEN3.A, R9.2
unnamed: R13.1, U5.5 (PROG)
unnamed: R14.1, RED5.K (C)
unnamed: R14.2, R15.1, U5.1 (STAT)
unnamed: GREEN5.A, R15.2
unnamed: R19.1, U7.5 (PROG)
unnamed: R20.1, RED7.K (C)
unnamed: R20.2, R21.1, U7.1 (STAT)
unnamed: GREEN7.A, R21.2
unnamed: R25.1, U9.5 (PROG)
unnamed: R26.1, RED9.K (C)
unnamed: R26.2, R27.1, U9.1 (STAT)
unnamed: GREEN9.A, R27.2
unnamed: R31.1, U11.5 (PROG)
unnamed: R32.1, RED11.K (C)
unnamed: R32.2, R33.1, U11.1 (STAT)
unnamed: GREEN11.A, R33.2
NW_CHARGE1: C4.1, CN1.P$2 (2), U1.3 (VBAT)
NW_CHARGE3: C6.1, CN3.P$2 (2), U3.3 (VBAT)
NW_CHARGE5: C10.1, CN5.P$2 (2), U5.3 (VBAT)
NW_CHARGE7: C14.1, CN7.P$2 (2), U7.3 (VBAT)
NW_CHARGE9: C18.1, CN9.P$2 (2), U9.3 (VBAT)
NW_CHARGE11: C22.1, CN11.P$2 (2), U11.3 (VBAT)

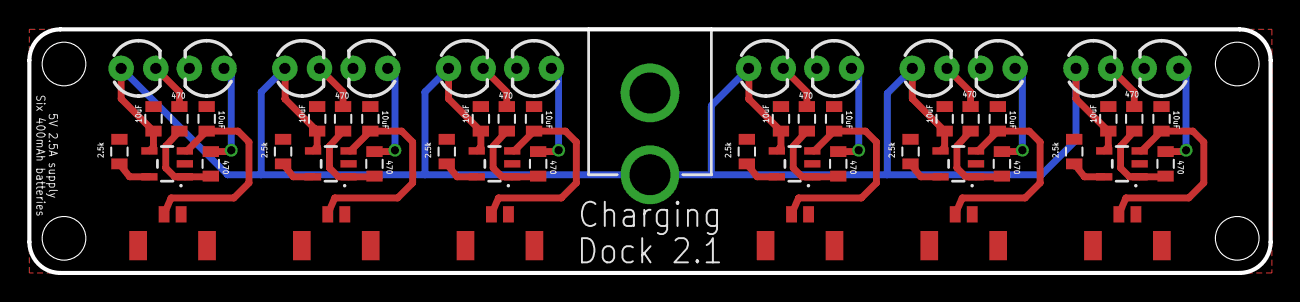
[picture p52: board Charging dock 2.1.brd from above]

Board: 2 copper layers, 91.0 x 17.9 mm, 55 parts (0 on the bottom side), 32 nets.

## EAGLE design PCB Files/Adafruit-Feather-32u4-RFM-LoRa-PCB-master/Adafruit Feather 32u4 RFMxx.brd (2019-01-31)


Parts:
ANT: HEADER-1X1ROUND; 1X01_ROUND
C1: 10uF; 0805-NO
C3, C6, C8: 10µF; 0805-NO
C7, C14: 1uF; 0603-NO
C9: 1uF; _0603MP
CHG: ORANGE; CHIPLED_0805_NOOUTLINE
D4: MBR120; SOD-123
IC1: ATMEGA32U4-MU; TQFN44_7MM
JP1: HEADER-1X16ROUND; 1X16_ROUND
JP3: HEADER-1X12; 1X12_ROUND
JP4: HEADER-1X2ROUND; 1X02_ROUND
L: RED; CHIPLED_0805_NOOUTLINE
R1, R3, R9: 100k; 0603-NO
R2: 1K; 0603-NO
R4, R5: 22; 0603-NO
R6: 100K; 0603-NO
R7: 2.2K; 0603-NO
R8: 10K\; 0603-NO
SW1: SPST_TACT-KMR2; KMR2
U2: AP2112-3.3; SOT23-5
U3: MCP73831T-2ACI/OT; SOT23-5
U4: RFM69HCW_SMT; RFMHCW_SMT
U$31, U$32: MOUNTINGHOLE2.5; MOUNTINGHOLE_2.5_PLATED
U$34, U$35: FIDUCIAL""; FIDUCIAL_1MM
X1: JSTPH; JSTPH2
X2: uFL; U.FL
X3: microUSB; 4UCONN_20329_V2
Y1: 8MHz; RESONATOR-SMD

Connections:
0: IC1.20 (PD2(INT2/RXD1)), JP1.3
1: IC1.21 (PD3(INT3/TXD1)), JP1.2
2: IC1.19 (PD1(INT1/SDA)), JP3.12
3: IC1.18 (PD0(INT0/OC0B/SCL)), JP3.11
5: IC1.31 (PC6(OC3A/!OC4A)), JP3.10
6: IC1.27 (PD7(OC4D/ADC10/T0)), JP3.9
9: IC1.29 (PB5(OC1A/ADC12/!OC4B)), JP3.8, R3.2, R6.1
10: IC1.30 (PB6(OC1B/OC4B/ADC13)), JP3.7
11: IC1.12 (PB7(OC0A/OC1C/RTS)), JP3.6
12: IC1.26 (PD6(T1/ADC9/!OC4D)), JP3.5
13: IC1.32 (PC7(ICP3/CLK0/OC4A)), JP3.4, R7.1
+3V3: C1.1, C7.1, C8.1, C9.1, IC1.6 (UCAP), IC1.14 (VCC), IC1.24 (AVCC), IC1.33 (PE2(!HWB)), IC1.34 (VCC1), IC1.44 (AVCC1), JP1.15, R1.2, U2.5 (OUT), U4.5P (VDD)
A0: IC1.36 (PF7(ADC7(TDI)), JP1.12
A1: IC1.37 (PF6(ADC6/TDO)), JP1.11
A2: IC1.38 (PF5(ADC5/TMS)), JP1.10
A3: IC1.39 (PF4(ADC4/TCK)), JP1.9
A4: IC1.40 (PF1(ADC1)), JP1.8
A5: IC1.41 (PF0(ADC0)), JP1.7
ANT: ANT.1, U4.1P (ANT), X2.3 (SIGNAL)
AREF: C14.1, IC1.42 (AREF), JP1.14
D4_RST: IC1.25 (PD4(ICP1/ADC8)), U4.14P (RESET)
D7_IRQ: IC1.1 (PE6(INT.6/AIN0)), U4.6P (DIO0)
D8_CS: IC1.28 (PB4(ADC11)), R1.1, U4.13P (NSS)
D+: IC1.4 (D+), R5.2
D-: IC1.3 (D-), R4.2
DIO1: JP1.1, U4.7P (DIO1)
DIO2: JP4.2, U4.8P (DIO2)
DIO3: JP4.1, U4.3P (DIO3)
DIO5: U4.15P (DIO5)
EN: JP3.2, R9.2, U2.3 (EN)
GND: C1.2, C3.2, C6.2, C7.2, C8.2, C9.2, C14.2, IC1.5 (UGND), IC1.15 (GND), IC1.23 (GND1), IC1.35 (GND2), IC1.43 (GND3), JP1.13, L.C, R6.2, R8.2, SW1.2 (S), SW1.4 (S1), U2.2 (GND), U3.2 (VSS), U4.2P (GND), U4.9P (GND), U4.16P (GND), X1.1, X2.1 (GND), X2.2 (GND), X3.BASE@1 (GND), X3.BASE@2 (GND), X3.GND, X3.SPRT@1 (GND), X3.SPRT@2 (GND), X3.SPRT@3 (GND), X3.SPRT@4 (GND), Y1.2
MISO: IC1.11 (PB3(PDO/MISO)), JP1.4, U4.10P (MISO)
MOSI: IC1.10 (PB2(PDI/MOSI)), JP1.5, U4.11P (MOSI)
unnamed: CHG.C, R2.1
unnamed: L.A, R7.2
unnamed: R2.2, U3.1 (STAT)
unnamed: R8.1, U3.5 (PROG)
unnamed: IC1.16 (XTAL2), Y1.3
unnamed: IC1.17 (XTAL1), Y1.1
unnamed: R5.1, X3.D+
unnamed: R4.1, X3.D-
RST: IC1.13 (/RESET), JP1.16, SW1.1, SW1.3 (P1)
SCK: IC1.9 (PB1(SCK)), JP1.6, U4.12P (SCK)
VBAT: C3.1, D4.A, JP3.1, R3.1, U3.3 (VBAT), X1.2
VBUS: C6.1, CHG.A, D4.C, IC1.7 (VBUS), JP3.3, R9.1, U2.1 (IN), U3.4 (VDD), X3.VBUS

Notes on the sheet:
POWER AND FILTERING
RESET
ATMEGA32U4 MCU
10K = 100mA
5.0K = 200mA
2.0K = 500mA
1.0K = 1000mA
BATTERY CHARGE & MONITOR
BREAKOUTS
RADIO MODULE



Board: 2 copper layers, 50.8 x 22.9 mm, 40 parts (4 on the bottom side), 44 nets.

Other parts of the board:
U$4: ADAFRUIT_5MM
U$5: FEATHERLOGO
U$6: PCBFEAT-REV-040
U$7: ADAFRUIT_3.5MM

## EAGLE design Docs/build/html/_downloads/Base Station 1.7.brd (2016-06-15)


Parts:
C1, C2: 47pF; CAP-PTH-SMALL
C5, C6, C7: 100nF; CAP-PTH-SMALL
C8: 4.7uF; CAP-PTH-SMALL
IC1: FT230XS; SSOP16
J1: POWER_JACKPTH; POWER_JACK_PTH
LED1: LED; PLCC-2
Q1: 2222A; TO92-EBC-OVAL
R1: 39; AXIAL-0.1
R2: 100; AXIAL-0.1
R3, R5, R15: 10k; AXIAL-0.1
R13, R16: 27; AXIAL-0.1
R14: 4.7k; AXIAL-0.1
U2: TINY85-20-DIP; DIP08
U$1: USB_SOCKET_MICRO_VERTHORIZONTAL; USB_HORZ_MICRO_SMD
U$3: RJ45; RJ45-8

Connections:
3.3VDC: U$3.7
5VDC: C5.1, C6.1, C8.1, IC1.12 (VCC), J1.PWR, LED1.ANODE (A), U2.8 (VCC), U$3.4
12VDC: U$3.6
85_RX: IC1.1 (TXD), U2.2 (PB3(ADC3))
85_TX: IC1.4 (RXD), U2.3 (PB4(ADC2))
GND: C1.1, C2.2, C5.2, C6.2, C7.2, C8.2, IC1.5 (GND), IC1.13 (GND), J1.GND, Q1.E, R3.P$2 (2), R5.P$2 (2), R15.P$1 (1), U2.4 (GND), U$1.G1, U$1.G2, U$1.P5, U$3.5
IN1: U$3.1
IN2: U$3.8
unnamed: Q1.C, R1.P$1 (1)
unnamed: LED1.CATHODE (C), R1.P$2 (2)
unnamed: R2.P$1 (1), U2.6 (PB1(MISO))
unnamed: Q1.B, R2.P$2 (2)
unnamed: C1.2, R16.P$1 (1), U$1.P2
unnamed: C2.1, R13.P$2 (2), U$1.P3
unnamed: R14.P$2 (2), U$1.P1
unnamed: IC1.9 (USBDM), R16.P$2 (2)
unnamed: C7.1, IC1.3 (VCCIO), IC1.10 (3V3OUT), IC1.11 (!RESET)
unnamed: IC1.15 (CBUS0), R14.P$1 (1), R15.P$2 (2)
unnamed: IC1.8 (USBDP), R13.P$1 (1)
OUT1: R3.P$1 (1), U2.7 (PB2(SCK/ADC1)), U$3.3
OUT2: R5.P$1 (1), U2.5 (PB0(MOSI)), U$3.2

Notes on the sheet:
NOSE DETECTOR
LICK DETECTOR
LED/BARRIER SOLENOID
REWARD SOLENOID
OUT1
IN1
FTDI_TX ARDUINO_RX


Board: 2 copper layers, 36.8 x 23.5 mm, 21 parts (1 on the bottom side), 17 nets.

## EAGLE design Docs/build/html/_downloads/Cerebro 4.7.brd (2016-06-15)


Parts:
C1: .1uF; 0603-CAP
C3: 2.2uF; 0805
C4: 10uF; 0805
D1: MBRM140T3G; POWERMITE
IC1: OPA237N; SOT23-5
INDICATOR_LED: LED; CHIP-LED0603
JP3: USB_MICROB_PLUG-PTH2; MICRO-B-TH
L1: 10uH; 1812
MIC2288: BOOST; SOT23-5
R1: 27; 0805
R2: 8.2; 0805
R3: 2k; 0805
R4, R9: 12k; 0805
R5: 20k; 0603-RES
R6, R7: 6.8k; 0805
R8: 20k; 0805
R10: 100; 0603-RES
S3: SWITCH-SPDTSMD2; SWITCH-SPDT-SMD
SDF: TSOP6238TT; TSOP6
T1: FJX3904TF; SOT323
U$1: DAC_LTC2630; SC-70
U$2: ATTINY84; SO14
U$3: SWITCH-MOMENTARY-NO; SWITCH_MOMENTARY_XS
U$4: EEPROM24C64A; SOT23-5
U$5: USB_SOCKET_MICRO_VERTHORIZONTAL; USB_HORZ_MICRO_SMD
U$7, U$8: BATT_TERMINAL

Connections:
8.68VDC: C4.1, D1.CATHODE (C), JP3.1, R4.2
BATT: C3.1, IC1.5 (V+), INDICATOR_LED.A, L1.P$2 (2), L1.P$4 (2), MIC2288.4 (EN), MIC2288.5 (VIN), R6.2, R7.2, R10.1, S3.2, U$1.VCC (VIN), U$2.1 (VCC), U$3.P$2 (2), U$4.4 (VCC)
GND: C1.2, C3.2, C4.2, IC1.2 (V-), JP3.2, JP3.P$1, JP3.P$2, MIC2288.2 (GND), R2.2, R3.1, R5.2, R8.2, R9.1, S3.3 (S), SDF.P$1 (1), SDF.P$2 (2), U$1.GND, U$2.14 (GND), U$4.2 (GND), U$5.G1, U$5.G2, U$7.P$1
MISO/TX: U$2.8 ((PCINT5/OC1B/MISO/DO/ADC5)PA5), U$5.P1
MOSI: R7.1, U$2.7 ((PCINT6/OC1A/SDA/MOSI/ADC6)PA6), U$4.3 (SDA), U$5.P5
unnamed: SDF.P$4 (4), U$2.12 ((PCINT1/AIN0/ADC1)PA1)
unnamed: U$1.CS/LD, U$2.10 ((PCINT3/T0/ADC3)PA3)
unnamed: IC1.3 (+IN), R8.1, U$1.VOUT
unnamed: JP3.4, S3.1 (O), U$8.P$1
unnamed: JP3.3, U$2.11 ((PCINT2/AIN1/ADC2)PA2)
unnamed: IC1.4 (-IN), R2.1, T1.3 (E)
unnamed: R9.2, U$2.13 ((PCINT0/AREF/ADC0)PA0), U$3.P$1 (1)
unnamed: INDICATOR_LED.C, R5.1
unnamed: IC1.1 (OUT), R1.2
unnamed: MIC2288.3 (FB), R3.2, R4.1
unnamed: R1.1, T1.2 (B)
unnamed: C1.1, R10.2, SDF.P$3 (3)
unnamed: JP3.5, T1.1 (C)
unnamed: U$1.SCK, U$2.3 ((PCINT9/XTAL2)PB1)
unnamed: D1.ANODE (A), L1.P$1 (1), L1.P$3 (1), MIC2288.1 (SW)
unnamed: U$1.SDI, U$2.2 ((PCINT8/XTAL1/CLKI)PB0)
RESET: U$2.4 ((PCINT11/~RESET/DW)PB3), U$5.P3
RX: U$2.6 ((PCINT7/ICP/OC0B/ADC7)PA7), U$5.P4
SCK: R6.1, U$2.9 ((PCINT4/T1/SCL/USCK/ADC4)PA4), U$4.1 (SCL), U$5.P2

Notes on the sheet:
BATTERY CHARGE <-----
+ANODE
-CATHODE
CURRENT CONTROL
BOOST CIRCUIT
LD+
LD-
CHG
GND
PHOTO



Board: 2 copper layers, 17.3 x 18.8 mm, 30 parts (9 on the bottom side), 24 nets.

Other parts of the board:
U$6: OSHW-LOGO-S

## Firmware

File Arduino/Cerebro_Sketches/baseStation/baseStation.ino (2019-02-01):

/*~~~~~~~~~~~~~~~~~~~~~~~~~~~~~~~~~~~~~~~~~~~~~~~~~~~~~~~~~~~~~~~~~~~~~~~~~~~~~~
MIT License

Copyright (c) 2015-2018 Andy S. Lustig

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
THE SOFTWARE IS PROVIDED "AS IS", WITHOUT WARRANTY OF ANY KIND, EXPRESS OR
IMPLIED, INCLUDING BUT NOT LIMITED TO THE WARRANTIES OF MERCHANTABILITY,
FITNESS FOR A PARTICULAR PURPOSE AND NONINFRINGEMENT. IN NO EVENT SHALL THE
AUTHORS OR COPYRIGHT HOLDERS BE LIABLE FOR ANY CLAIM, DAMAGES OR OTHER
LIABILITY, WHETHER IN AN ACTION OF CONTRACT, TORT OR OTHERWISE, ARISING FROM,
OUT OF OR IN CONNECTION WITH THE SOFTWARE OR THE USE OR OTHER DEALINGS IN THE
SOFTWARE.
~~~~~~~~~~~~~~~~~~~~~~~~~~~~~~~~~~~~~~~~~~~~~~~~~~~~~~~~~~~~~~~~~~~~~~~~~~~~~~~*/

//Documentation for this project can be found at https://karpova-lab.github.io/cerebro/

#include <Radio.h>  //https://github.com/LowPowerLab/RFM69
#include <SPI.h>
#include <EEPROM.h>
#include <avr/wdt.h>

#define CHANNEL_ADDRESS 0 //holds uint8_t, 1 byte wide
#define RIG_ROOM_ADDRESS 1 //holds uint8_t, 1 byte wide
#define RIG_NUM_ADDRESS 2 //holds uint8_t, 1 byte wide

const uint8_t VERSION = 57; //2019-01-31

const uint8_t LED = 13;
const uint8_t TRIGGER_PIN = 6;
const uint8_t STOP_PIN = 5;

uint8_t netID;
uint8_t rigRoom;
uint8_t rigNum;

Radio radio(8,7); //slave select pin, interrupt pin
WaveformData newWaveform;
WaveformData currentWaveform;
DiodePowers newDiodePowers;
DiodePowers currentDiodePowers;
IntegerPayload integerMessage;
Info cerebroInfo;
Feedback diodeStats;

uint32_t  valsFromParse[5];
uint32_t  startTime = 0;
uint32_t  spamFilter = 0;
uint32_t  triggerClock = 0;
uint16_t  msgCount = 0;
bool      ignoreFilter = false;
bool      warningsOn = true;

void setup() {
  Serial1.begin(57600);
  delay(10);
  pinMode(LED, OUTPUT);

  EEPROM.get(CHANNEL_ADDRESS,netID);
  radio.radioSetup(1,false,netID); //nodeID, autopower off;
  pinMode(TRIGGER_PIN,INPUT);
  pinMode(STOP_PIN,INPUT);
  startTime = millis();
  newSession();
}

void loop() {
  ////////////Receive Message From Bcontrol
  if (digitalRead(TRIGGER_PIN)) {
    while(digitalRead(TRIGGER_PIN)){
      //wait until signal goes low
    }
    triggerCommandReceived();
  }
  //if we read a high signal on pin 6, send a stop command to cerebro
  if (digitalRead(STOP_PIN)) {
    while(digitalRead(STOP_PIN)){
      //wait until signal goes low
    }
    stopCommandReceived();
  }

  ///////////Receive Message From Xavier//////////////////
  if (Serial1.available()){
    char msg = Serial1.read();
    if (msg=='W'){  //parse data then send new waveform
      parseData();
      sendWaveformUpdate();
    }
    else if (msg=='D'){  //parse data then send new power
      parseData();
      sendDiodePowerUpdate();
    }
    else if (msg=='S' || msg == 'L' || msg == 'R' ||  msg == 'l' ||  msg == 'r'){ //parse data then send radio message with integer
      parseData();
      delay(500);
      sendMsgAndVal(msg,valsFromParse[0]);
    }
    else if (msg=='T'){
      triggerCommandReceived();
    }
    else if (msg=='A'){
      stopCommandReceived();
    }
    else if(msg=='M'){
      requestMissed();
    }
    else if(msg=='N'){
      newSession();
    }
    else if (msg=='K'){
      parseData();
      uint8_t newNetworkID = valsFromParse[0];
      Serial1.print("\nChanging to channel:");
      Serial1.println(newNetworkID);
      EEPROM.update(CHANNEL_ADDRESS, newNetworkID);
      Serial1.println("Restarting...");
      wdt_enable(WDTO_15MS);  // turn on the WatchDog timer
      while(1){}              // do nothing and wait for the reset
    }
    else if (msg=='X'){
      parseData();
      rigRoom = valsFromParse[0];
      rigNum = valsFromParse[1];
      Serial1.print("\nBase Station is now associated with Rig:");
      Serial1.print(rigRoom);Serial1.print(".");Serial1.println(rigNum);
      EEPROM.update(RIG_ROOM_ADDRESS, rigRoom);
      EEPROM.update(RIG_NUM_ADDRESS, rigNum);
    }
    else if(msg=='?'){
      Serial1.print("Channel: ");
      Serial1.println(netID);
      Serial1.print("Base Version,");Serial1.print(VERSION);newline();
    }
    else if (msg=='P'){ 
      uint16_t waveDuration = 5000;
      uint32_t waveClock = millis();
      Serial1.print("Blinking...");newline();
      while((millis() - waveClock) < waveDuration){
        delay(100);
        digitalWrite(LED,HIGH);
        delay(100);
        digitalWrite(LED,LOW);
      }
      Serial1.print("....done");newline();
    }
    else if (msg!='\n'){
      relayMsg(msg);
    }
  }

  ///////////Receive Message From Cerebro///////
  if (radio.receiveDone()){
    switch (radio.DATALEN) {
      case sizeof(cerebroInfo):
        if (radio.ACKRequested()){
          radio.sendACK();
        }
        cerebroInfo = *(Info*)radio.DATA;
        printCerebroInfo();
        break;
      case sizeof(currentDiodePowers):
        if (radio.ACKRequested()){
          radio.sendACK();
        }
        currentDiodePowers = *(DiodePowers*)radio.DATA;
        printDiodePowers(currentDiodePowers,true);
        break;
      case sizeof(currentWaveform):
        if (radio.ACKRequested()){
          radio.sendACK();
        }
        currentWaveform = *(WaveformData*)radio.DATA;
        if (currentWaveform.trainDur>0){
          spamFilter = currentWaveform.startDelay + currentWaveform.trainDur;
          warningsOn = false;
        }
        else{
          spamFilter = currentWaveform.startDelay + currentWaveform.onTime;
          warningsOn = true;
        }
        printWaveform(currentWaveform,true);
        break;
      case sizeof(diodeStats):
        if (radio.ACKRequested()){
          radio.sendACK();
        }
        diodeStats = *(Feedback*)radio.DATA;
        printDiodeStats();
        break;
      case  sizeof(integerMessage):
        if (radio.ACKRequested()){
          radio.sendACK();
        }
        integerMessage = *(IntegerPayload*)radio.DATA;
        if(integerMessage.variable == 'B'){
          printBattery(integerMessage.msgCount,integerMessage.value);
        }
        else if (integerMessage.variable == 'M'){
          Serial1.print("Total Missed,");Serial1.print(integerMessage.value);newline();
        }
        else if (integerMessage.variable =='m'){
          Serial1.print("Missed Message Index,");Serial1.print(integerMessage.value);newline();
        }
        else if (integerMessage.variable == 'Y'){
          Serial1.print("Cerebro turned on and connected,");Serial1.print(integerMessage.value);//print time it took to startup and send connection message.
        }
        break;
    }
  }
}

void parseData(){
  char msgData[30] = "";
  Serial1.readBytesUntil('\n',msgData,30);
  char* msgPointer;
  msgPointer = strtok(msgData,",");
  char i = 0;
  while (msgPointer!=NULL){
    valsFromParse[i] = atol(msgPointer);
    msgPointer = strtok(NULL,",");
    i++;
  }
}

void sendMsgAndVal(char msg,unsigned int val){
  integerMessage.variable = msg;
  integerMessage.value = val;
  Serial1.print("\nSending '"); Serial1.print(msg);Serial1.print("' ") ;Serial1.print(integerMessage.value);Serial1.print("...");
  if (radio.sendWithRetry(CEREBRO, (const void*)(&integerMessage), sizeof(integerMessage),5)){
    Serial1.print("data received");newline();
  }
  else{
    Serial1.print("*X&data send fail");newline();
  }
}

void newSession(){
  startTime = millis();
  msgCount = 0;
  Serial1.print("\n*BaseOn&Base Version,");Serial1.print(VERSION);newline();
  uint32_t theVals[1] = {netID};
  sendDataToXavier("Base Channel",theVals,1);
  Serial1.print("Base Channel,");Serial1.print(netID);newline();
  
  EEPROM.get(RIG_ROOM_ADDRESS, rigRoom);
  EEPROM.get(RIG_NUM_ADDRESS,rigNum);
  uint32_t rigVals[2] = {rigRoom,rigNum};
  sendDataToXavier("Rig Number",rigVals,2);

  char msg = 'N';
  if (radio.sendWithRetry(CEREBRO, &msg, 1, 3)){
    // Serial1.print("Connected!");
  }
  else{
    Serial1.print("*X&Error communicating with Cerebro\n\n");
  }
}

void relayMsg(char msg){
  if (radio.sendWithRetry(CEREBRO, &msg, 1, 0)){  // 0 = only 1 attempt, no retries
  }
  else{
    Serial1.print("*X&");
    printTime();Serial1.print("Tried Sending ''");Serial1.print(msg);
    Serial1.print("'', ACK not received");newline();
  }
}

void printCerebroInfo(){
  uint32_t theVals[2] = {cerebroInfo.firmware, cerebroInfo.serialNumber};
  sendDataToXavier("Cerebro Info",theVals,2);
  Serial1.print("Cerebro Version,");Serial1.print(cerebroInfo.firmware);newline();
  Serial1.print("Serial Number,");Serial1.print(cerebroInfo.serialNumber);newline();
}

void printDiodePowers(DiodePowers printPower,  bool response){
  printTime();
  if(response){
    Serial1.print("[");Serial1.print(printPower.msgCount);Serial1.print(']');
  }
  else{
    Serial1.print(msgCount);
  }
  uint32_t theVals[2] = {printPower.lSetPoint, printPower.rSetPoint};
  sendDataToXavier("Diode Powers",theVals,2);
  printToBaseMonitor("Diode Powers",theVals,2);
}

void printBattery(uint16_t batteryMsgCount, uint8_t batteryStatus){
  printTime();
  Serial1.print("[");Serial1.print(batteryMsgCount);Serial1.print("]");
  uint32_t theVals[] = {batteryStatus};
  uint8_t numElements = sizeof(theVals)/sizeof(uint32_t);

  sendDataToXavier("Battery",theVals,numElements);
  printToBaseMonitor("Battery",theVals,numElements);
}

void printWaveform(WaveformData wave, bool response){
  printTime();
  uint32_t theVals[] = {wave.startDelay, wave.onTime, wave.offTime, wave.trainDur, wave.rampDur};
  uint8_t numElements = sizeof(theVals)/sizeof(uint32_t);

  sendDataToXavier("Waveform",theVals,numElements);
  if(response){
    Serial1.print("[");Serial1.print(wave.msgCount);Serial1.print(']');
  }
  else{
    Serial1.print(msgCount);
  }
  printToBaseMonitor("Waveform",theVals,numElements);
}

void printDiodeStats(){
  printTime();
  Serial1.print("[");Serial1.print(diodeStats.msgCount);Serial1.print("]");
  uint32_t theVals[6] = {currentDiodePowers.lSetPoint, diodeStats.leftFBK, diodeStats.leftDAC, currentDiodePowers.rSetPoint, diodeStats.rightFBK, diodeStats.rightDAC};
  printToBaseMonitor("Feedback",theVals,6);
  if (diodeStats.leftDAC>3000 && warningsOn){
    Serial1.print("Warning: Left DAC value of ");Serial1.print(diodeStats.leftDAC);Serial1.print(" is suspicously high\n");
  }
  if (diodeStats.rightDAC>3000 && warningsOn){
    Serial1.print("Warning: Right DAC value of ");Serial1.print(diodeStats.rightDAC);Serial1.print(" is suspicously high\n");
  }
  int32_t leftDiff = (int32_t)currentDiodePowers.lSetPoint-(int32_t)diodeStats.leftFBK;
  int32_t rightDiff = (int32_t)currentDiodePowers.rSetPoint-(int32_t)diodeStats.rightFBK;
  uint8_t diffThresh = 20;
  if ((abs(leftDiff)>diffThresh) && warningsOn){
    Serial1.print("Warning: Large difference (");Serial1.print(leftDiff);Serial1.print(") between left diode's set point and feedback\n");   
  }
  if ((abs(rightDiff)>diffThresh) && warningsOn){
    Serial1.print("Warning: Large difference (");Serial1.print(rightDiff);Serial1.print(") between right diode's set point and feedback\n");  
  }
}

void sendWaveformUpdate(){
  newWaveform.startDelay = valsFromParse[0];
  newWaveform.onTime = valsFromParse[1];
  newWaveform.offTime = valsFromParse[2];
  newWaveform.trainDur = valsFromParse[3];
  newWaveform.rampDur = valsFromParse[4];
  newWaveform.msgCount = msgCount++;
  printWaveform(newWaveform,false);
  if (radio.sendWithRetry(CEREBRO, (const void*)(&newWaveform), sizeof(newWaveform))){
    currentWaveform = newWaveform;
    ignoreFilter = true;    
  }
  else{
    Serial1.print("*X&Waveform Update Failed\n");
  }
}

void sendDiodePowerUpdate(){
  newDiodePowers.lSetPoint = valsFromParse[0];
  newDiodePowers.rSetPoint = valsFromParse[1];
  newDiodePowers.msgCount = msgCount++;
  printDiodePowers(newDiodePowers, false);
  if (radio.sendWithRetry(CEREBRO, (const void*)(&newDiodePowers), sizeof(newDiodePowers))){
    currentDiodePowers = newDiodePowers;
  }
  else{
    Serial1.print("*X&Diode Power Update Failed\n");
  }
}
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

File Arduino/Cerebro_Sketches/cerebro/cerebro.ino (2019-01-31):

/*~~~~~~~~~~~~~~~~~~~~~~~~~~~~~~~~~~~~~~~~~~~~~~~~~~~~~~~~~~~~~~~~~~~~~~~~~~~~~~
MIT License

Copyright (c) 2015-2018 Andy S. Lustig

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
THE SOFTWARE IS PROVIDED "AS IS", WITHOUT WARRANTY OF ANY KIND, EXPRESS OR
IMPLIED, INCLUDING BUT NOT LIMITED TO THE WARRANTIES OF MERCHANTABILITY,
FITNESS FOR A PARTICULAR PURPOSE AND NONINFRINGEMENT. IN NO EVENT SHALL THE
AUTHORS OR COPYRIGHT HOLDERS BE LIABLE FOR ANY CLAIM, DAMAGES OR OTHER
LIABILITY, WHETHER IN AN ACTION OF CONTRACT, TORT OR OTHERWISE, ARISING FROM,
OUT OF OR IN CONNECTION WITH THE SOFTWARE OR THE USE OR OTHER DEALINGS IN THE
SOFTWARE.
~~~~~~~~~~~~~~~~~~~~~~~~~~~~~~~~~~~~~~~~~~~~~~~~~~~~~~~~~~~~~~~~~~~~~~~~~~~~~~~*/
const uint8_t VERSION = 96; // 2018-11-30
//~~~~~~~~~~~~~~~~~~~~~~~~~~~~~~~~~~~~~~~~~~~~~~~~~~~~~~~~~~~~~~~~~~~~~~~~~~~~~~~
/*
        ______                   __
       / ____/___   _____ ___   / /_   _____ ____
      / /    / _ \ / ___// _ \ / __ \ / ___// __ \
     / /___ /  __// /   /  __// /_/ // /   / /_/ /
     \____/ \___//_/    \___//_.___//_/    \____/

Documentation for this project can be found at https://karpova-lab.github.io/cerebro/
*/
#include <EEPROM.h>
#include <LaserDiode.h>
#include <SparkFunBQ27441.h>      //https://github.com/sparkfun/SparkFun_BQ27441_Arduino_Library
#include <Radio.h>                //https://github.com/LowPowerLab/RFM69
#include <LowPower.h>             //https://github.com/LowPowerLab/LowPower
#include <avr/wdt.h>

#define SERIAL_NUMBER_ADDRESS 0
#define CHANNEL_ADDRESS 1
#define WAVEFORM_ADDRESS 2
#define LEFT_SETPOINT_ADDRESS 16
#define RIGHT_SETPOINT_ADDRESS 18
#define MISSING_ARRAY_ADDRESS 20

WaveformData waveform;
DiodePowers diodePwrs;
IntegerPayload integerMessage;
Info cerebroInfo;
Feedback diodeStats;

uint16_t meterVal = 0;

const uint8_t amberLED = A0; //32u4 pin 36
const uint8_t greenLED = 12; //32u4 pin 26
const uint8_t userBTN = 6; //32u4 pin 27
LaserDiode right(&DDRB,&PORTB,0,A4);
LaserDiode left(&DDRD,&PORTD,2,A2);

uint8_t channel;
Radio radio(7,1); //slave select pin, interrupt pin
uint16_t msgCount = 0;
uint16_t missedCount = 0;
uint16_t trigCount = 0;
uint8_t batteryUpdateFrequency = 10;
bool reportBatteryFlag = false;
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

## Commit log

2016-06-15 Initial commit.
    [7segment.xlsx, Base Station 1.7.brd, Base Station 1.7.sch, Behavior box top.dxf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]
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2016-09-02 Base station PCB update: Changed to reinforced micro usb for more solid connection. Made 47 pF labels visible. Added OSH logo moved FTDI chip to bottom for easier soldering of the chip and the micro 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
    [Base Station 1.8.brd, Base Station 1.8.sch, Base station 1.8.brd, Base station 1.8.sch]
2016-09-02 Fixed broken PCB file links on base station documentation page
2016-09-02 This is annoying, git isn't recognizing case sensitive changes to filenames. this is a temporary deletion of Base station folder
    [Base station 1.8.brd, Base station 1.8.sch]
2016-09-02 PCB links in the base station documentation should now be fixed!
    [Base Station 1.8.brd, Base Station 1.8.sch]
2016-09-21 Cerebro PCB update to 4.8: - npn emitter resistor was 8.2ohm, now 6.8 ohm - removed push button resistor and changed to internal pullup resistor on MCU - switched to from 0805 to 0603 for all resisto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
    Updated cerebro.ino:
    - pushbutton now gives a low signal when pressed.
    - Arduino IDE update to 1.6.11 effected the delayMicroseconds(), thereby breaking the IR communication. Changed the irResolution to 4 in order to fix.
    Updated docs to have Cerebro 4.8 files
    [Cerebro 4.8.brd, Cerebro 4.8.sch]
2016-09-28 Now just send a calibrate signal to begin calibrate routine, no longer have to reflash firmware with #CALIBRATE defined. New arduino IDE effected IR timing. fixed Cerebro library accordingly.
2016-09-29 Power level is now a constant. Can now wireless adjust start delay. No longer constant, dictated by #STARTDELAY definition Fixed bug where on delay was cutting into the waveform duration. Updated Xav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
2016-10-10 fixed parse file so that it gives the delay parameter instead of the power level parameter in the summary.txt
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2016-10-18 Can now send calibration routine start. Fixed bug where printed Cerebro parameters weren't activating a dialog box every time.
2016-10-20 Added Cerebro# and LD# to Power Level dialog. Cerebro# and LD# are now automatically sent when updating the fade vector Calibration script now finds peaks that are closer to the center of the pulses 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
2016-10-21 Documentation update. Added implant characterization instructions. Updated Xavier Deployment.zip download Updated Xavier Waveform explanation. Added instructions for checking Cerebro's onboard parame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
    [pulse parameters.dxf]
2016-10-21 Another doc update
    [memory layout.xlsx]
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2016-10-31 Increased delay leading up to calibration routine. Fixed bug where EEPROM waveform parameters were being used during calibration routine. Removed isMaxed conditional from calibration routine
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2016-11-08 Can now receive powerTest trigger that powers the laser at a temporary power level. Fixed bug introduced in c4e7b27 on September 29. "ms" being printed to log breaks the "compare" function in the log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
2016-11-21 cleaned up calibrateRoutine triggerEvent() now has feedback variable that replaces the #ifdef MCUBE logic. removed some excessive printing during calibration mode.
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2016-11-29 If using MCUBE mode, you can now change power level using powertest command from Cerebro library. fixed bug where powerLevel was grabbing the wrong value from EEPROM.
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2016-12-02 Fixed bug where MCUBE power level wasn't getting updated after first update.
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2016-12-20 Doc update
    [memory layout.xlsx]
2017-01-04 Ramp down checkbox wasn't being unchecked if it previously was checked and then a new Cerebro was connected that didn't have a ramp down. Debug checkbox is now unchecked after settings dialog is exit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
2017-01-09 Charging Dock and Utility Shield revisions. Doc Update
    [Charging Dock 1.4.brd, Charging Dock 1.4.sch, Charging Dock 1.8.brd, Charging Dock 1.8.sch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]
2017-01-10 fixed cerebro BOM in docs. updated PCB files that I forgot to commit last commit.
    [Charging Dock 1.4.brd, Charging Dock 1.4.sch, Charging Dock 1.8.brd, Charging Dock 1.8.sch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]
2017-01-13 fixed bug where “Connect to Downloader” button was remaining checked even after serial port was disconnected
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2017-02-04 temporary rename
    [Utility Shield 1.4.brd, Utility Shield 1.4.sch]
2017-02-04 Another rename. This should fix read the docs broken link
    [Utility Shield 1.4.brd, Utility Shield 1.4.sch]
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2017-04-03 Renamed Docs folder to Documentation Source
    [Base Station 1.8.brd, Base Station 1.8.sch, Behavior box top.dxf, Cerebro 4.8.brd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]
2017-04-03 Docs now available on github pages
    [Base Station 1.8.brd, Base Station 1.8.sch, Behavior box top.dxf, Cerebro 4.8.brd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]
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2017-05-12 Xavier and parsing updates Xavier: -Added option to show histogram at the end of session. -Updated documentation web address -Base station filter should not include fade time!!! Parsing scripts: -Mad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
2017-06-20 diode pairing scripts
    [comparison.xlsx]
2017-06-27 remove diode pairing folder
    [comparison.xlsx]
2017-06-28 remove build folder
    [Base Station 1.8.brd, Base Station 1.8.sch, Behavior box top.dxf, Cerebro 4.8.brd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]
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2017-09-12 added calibration routine. combined diode power is now correctly a sum of it's component parts.
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2017-09-26 removed unnecessary sketches and libraries
    [7segment.xlsx]
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2017-10-11 remove docs temporarily
    [Base Station 1.8.brd, Base Station 1.8.sch, Behavior box top.dxf, Cerebro 4.8.brd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]
2017-10-11 update PCB files
    [Adafruit Feather 32u4 RFMxx.brd, Adafruit Feather 32u4 RFMxx.sch, Base Station 1.8.brd, Base Station 1.8.sch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]
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2017-10-19 fixed bug in sending and printing missed count
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2017-10-19 footprint for feather. probably not neccesary, better to velcro base station to side of box
    [Behavior box top.dxf]
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2017-10-20 no longer clear monitor after cerebro ping. fixed bug where laser report was happening after abort fade.
2017-10-20 2.0 docs rough rough draft
    [F0000CH1.CSV, F0000CH2.CSV, F0001CH1.CSV, F0001CH2.CSV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]
2017-10-20 rename docs
    [memory layout.xlsx, pulse parametersv2.dwg, pulse parametersv2.dxf, tables.xlsx]
2017-10-20 fix watchdog timer from going because eeprom was taking a long time to be written to, because filtered stops were being counted towards the msgcount
2017-10-20 fixed folder name
    [F0000CH1.CSV, F0000CH2.CSV, F0001CH1.CSV, F0001CH2.CSV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]
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2017-11-01 temp commit
    [tables.xlsx]
2017-11-01 fixed battery reporting bug
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2017-11-22 Lasercut jig for programming Cerebro
    [jig.dxf]
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2017-11-29 Added BOMs for Cerebro, Head Implant, and Base station
    [Base Station 2.1.brd, Base Station 2.1.sch, F0000CH1.CSV, F0000CH2.CSV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]
2017-11-29 removed references to missing images. Modified makefile to clean docs/ folder
    [tables.xlsx]
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2017-12-08 Added some pictures to "Overview" Section", updated estimated cost. Added updated "Xavier" section.
    [pulse parametersv2.dwg, pulse parametersv2.dxf, tables.xlsx]
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2018-02-28 some lasercut files. eagle library update
    [3axis plate.dxf, fiber alignment jig.dxf]
2018-03-02 BOM update. replaced jst-sr connector with molex microclasp. Updated Cerebro PCB from 5.4 to 5.6
    [tables.xlsx]
2018-03-02 Updated Base Station BOM. Fixed some typos
    [tables.xlsx]
2018-03-02 update table generator script
    [tables.xlsx]
2018-03-13 Minor Xavier update. Docs should now have latest Deployment.zip
    [tables.xlsx]
2018-03-14 tableGenerator update
    [tables.xlsx]
2018-03-20 updates to implant documentation
    [Fiber guide_1,5mm gap.dxf]
2018-03-21 added back datasheets
    [Base Station 1.8.brd, Base Station 1.8.sch, Behavior box top.dxf, Cerebro 4.8.brd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]
2018-03-23 added charging dock documentation
    [tables.xlsx]
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2018-04-26 Added pogo connector resources. Added instructions for burning bootloader onto Cerebro
    [tables.xlsx]
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2018-05-02 Updated overivew text and added pictures. Added links to USB drivers.
    [tables.xlsx]
2018-05-08 Updates for Cerebro 5.8. Revamped session start dialog. Can now easily connect to any Cerebro and can easily setup new Cerebros.
    [tables.xlsx]
2018-08-16 Updated to latest PCB files
    [Base Station 2.4.brd, Base Station 2.4.sch, Charging dock 2.1.brd, Charging dock 2.1.sch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]
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2018-12-04 doc update. Xavier 3.9.0 , base station 2.5, cerebro 5.8
    [Base Station 2.4.brd, Base Station 2.4.sch, Base Station 2.5.brd, Base Station 2.5.sch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]
2018-12-10 updated Xavier deployment download to version 1.31.0
    [Base Station 1.8.brd, Base Station 1.8.sch, Behavior box top.dxf, Cerebro 4.8.brd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]
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2019-01-10 added double underscore to links to remove sphinx build warnings about duplicate links added line after github url to remove another build warning edited bom table to account for when a datasheet pdf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
    [tables.xlsx]
2019-02-01 Sort of back to normal?
    [memory layout.xlsx, pulse parametersv2.dwg, pulse parametersv2.dxf, tables.xlsx]
2019-03-28 Documentation update.
    [Cerebro 4.8.sch, Implant 4.4.brd, tables.xlsx]
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2022-06-13 updated overview and added license
    [Fiber guide_1,5mm gap.dxf]

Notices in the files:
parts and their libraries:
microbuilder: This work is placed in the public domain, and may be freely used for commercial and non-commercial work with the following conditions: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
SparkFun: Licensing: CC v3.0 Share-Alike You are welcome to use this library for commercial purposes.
